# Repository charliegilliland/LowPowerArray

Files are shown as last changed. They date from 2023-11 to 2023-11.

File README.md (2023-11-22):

# LowPowerArray

This repository contains the hardware design files and firmware for a low-power acoustic array.
Up to 8 channels of microphone data are sampled at 48kHz and saved to an SD card.
Data acquisition is synchronized to UTC time with a GPS.

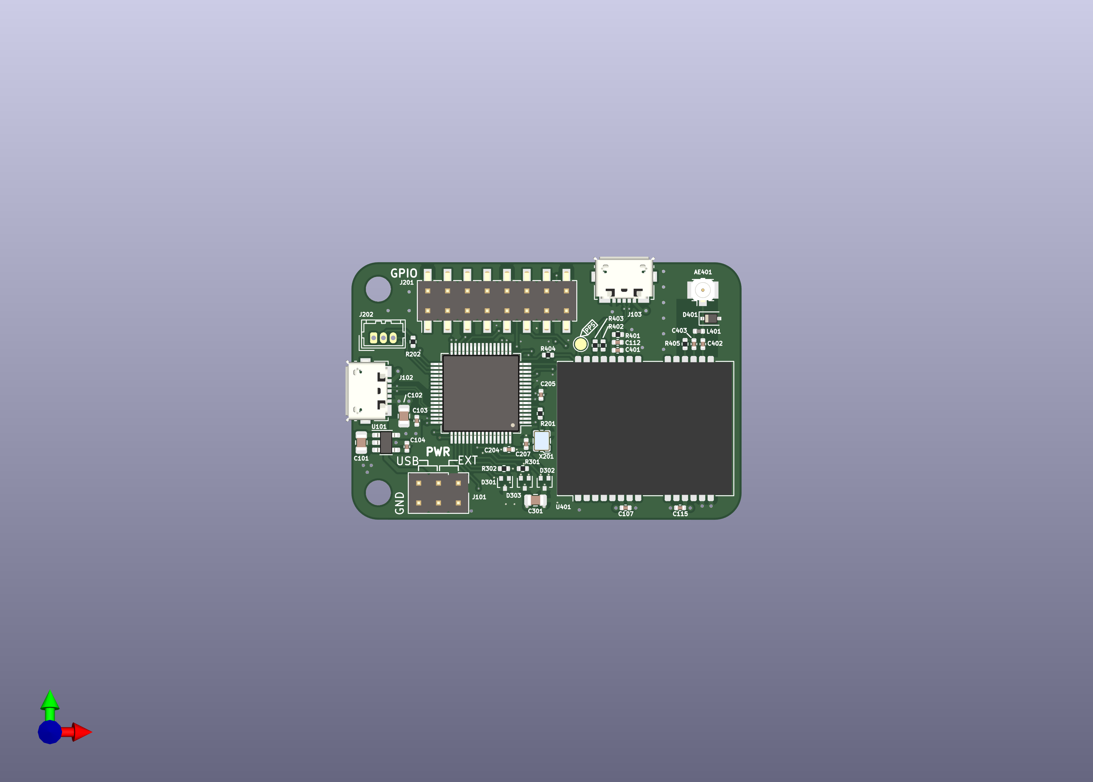
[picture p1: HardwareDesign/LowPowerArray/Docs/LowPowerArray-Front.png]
LowPowerArray


## Theory of Operation

### Power
The LowPowerArray can be powered via USB or pin headers on J101.
The power source is selected by placement of a jumper on J101.
A servo-style connector can be plugged into J101.
Refer to the schematics in [HardwareDesign](HardwareDesign/LowPowerArray/) for pin descriptions.

### Modes
There are two modes of operation: Manual and Automatic.
The mode is selected with a jumper on J201.

In Manual mode (jumper present) data acquisition is started and stopped using the pushbutton connected to J202.

In Automatic mode (jumper not present) data acquisition will begin automatically once power is applied and the GPS is locked.
If the button is pressed while in Automatic mode, the data acquisition will be stopped and the device will revert to Manual mode.

### Status
At startup, the device will wait for a GPS lock, unless ```GPS_WAIT_LOCK``` is defined as 0 (useful for lab testing).
When the GPS is locked, the LED will quickly illuminate several times, indicating that it is ready to start data acquisition.

While the data acquisition is running, the LED will illuminate every other second.

Status messages will be printed over the UART pins on J201, and also over USB via the virtual COM port.

### Programming
The STM32 microcontroller is programmed via SWD using the pins SWDIO, SWCLK, NRST on J201.
A Nucleo development board, or dedicated programmer, can be used to program the device.

### Microphone Connections
The 10-pin FFC connector, J1, is used to connect to a microphone board.

Alternatively, the BCLK, FSYNC, and DATA pins are available as pin headers on J201.

### SD Card Storage
Audio and GPS data are stored on the microSD card.
The card must be formatted as exFAT.

At startup, the device will create a new directory with the prefix ```filesXXXX```, where XXXX is a number: i.e. ```files0001```.

Audio and GPS files will be stored in the newly created directory, with file names ```audioXXXX.pcm``` and ```gpsXXXX.txt```.
Audio data is raw PCM format, with 8 channels and 32-bit word length.
GPS data is stored as plain text NMEA sentences, exactly as it is received from the GPS module.

GPS data can be tied to the audio data by matching the file numbers.
There is one pair of GPS messages for each second, where the first pair of GPS messages is tied to the first frame of audio in the audio file.

### GPS Module
The GPS module provides the PPS (pulse per second) and BCLK (bit clock) signals, as well as location and time via NMEA messages over UART.

Be sure to program the GPS module using the configuration file ```charlie-m8t-lowpower.txt```.

There is a battery connector, labeled BT101, which can provide backup power to the GPS.
The battery should be a 3v coin-cell or equivalent, and are commonly available as CMOS batteries.

Be sure to plug in the battery with the correct polarity (+ and - are marked on the v2 board).

If for some reason the GPS is not used, an auxiliary clock source can be used by populating a 12.288MHz crystal oscillator X501.
If this is used, select the clock source by placing R502 instead of R501.
Using the auxiliary clock source will require firmware changes to account for the missing PPS signal, and no GPS messages.
At time of writing this is not supported by the firmware.

For debugging purposes, when GPS lock is not required to start data acquisition, go to the file ```gps_mgr.h``` and change ```GPS_WAIT_LOCK``` to 0,
and re-program the device.
This will allow you to test the device in the lab, where GPS signals are not available.

## Programming Guide

### main.c
The file [main.c](Firmware/Core/Src/main.c) mostly contains code generated by CubeIDE. This file simply initializes the peripherals, and calls the user_app_init and user_app_loop functions.
This file should not have to be changed.

### user_app.c
The file [user_app.c](Firmware/Core/Src/user_app.c) contains the high-level runtime behavior of the device.
This includes the main endless while loop, the data acquisition loop, and button and PPS callback functions.

The endless while loop in user_app_loop implements the state diagram described below.

### aud_mgr.h
The file [aud_mgr.h](Firmware/Core/Inc/aud_mgr.h) contains the audio-specific code.
This uses the SAI peripheral in DMA mode, so that audio data can be received 'in the background' while the CPU is working on other tasks.

The ```HAL_SAI_RxCpltCallback``` is called by the hardware when a buffer of new data is ready.
In this function, the DMA buffer pointer is changed to the next buffer in the ring buffer.
The ring buffer allows for multiple buffers to be stored before they are written to the SD card. 

If there is an SAI error, or ring buffer overflow, the data acquisition will be stopped and the PPS will be re-synchronized.

### sd_mgr.h
The file [sd_mgr.h](Firmware/Core/Inc/sd_mgr.h) contains the sd card-specific code.
This code contains functions for starting new files, and writing to existing files.

### gps_mgr.h
The file [gps_mgr.h](Firmware/Core/Inc/gps_mgr.h) contains the GPS-specific code.
GPS data is received over USART2 in DMA mode.

When the GPS messages have been received, the ```HAL_UARTEx_RxEventCallback``` function will be called by the hardware.
The received messages will be copied to local buffers, and the RX will be restarted to handle the next message.

### inline functions
Many of the functions implemented in the peripheral files are ```inline``` functions.
This is done for execution speed: basically instead of actually calling those functions,
the compiler will copy that code to where the function was called.

### DAQ State Diagram
This figure describes the various states that the device can be in, and the events that cause a state change.
The ```daq_stat``` variable declared in user_app.c is used to read and change state in the code.

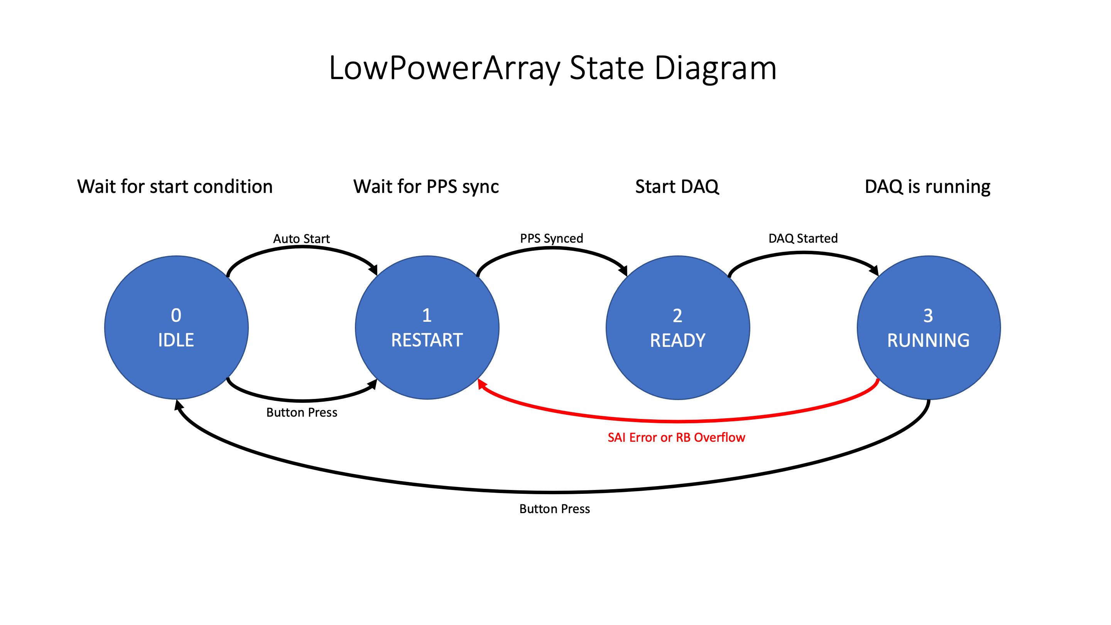
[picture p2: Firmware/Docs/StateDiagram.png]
State Diagram


## Future Work

### Directory / file naming
It would probably be better to name the files using the UTC date and time as received from the GPS.
This would require parsing each GPS message, and some more logic for dealing with the timing in creating the files.

### Control and monitoring over UART / USB
It might be possible to start and stop the data acquisition over UART or USB, though I haven't explored this in detail.
This would allow a remote computer, such as a raspberry pi, to control the data acquisition.
Additionally, a telemetry radio could be connected to the UART serial port for remote status monitoring and control.

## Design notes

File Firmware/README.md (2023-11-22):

# LowPowerArrayFirmware

This repository contains the STM32CubeIDE project files used on the LowPowerArray board.

## Theory of Operation

### Power
The LowPowerArray can be powered via USB or pin headers on J101.
The power source is selected by placement of a jumper on J101.
A servo-style connector can be plugged into J101.
Refer to the schematics in [Charlie-KiCad](https://github.com/UM-NCPA/Charlie-KiCad/tree/main/LowPowerArray_v2) for pin descriptions.

### Modes
There are two modes of operation: Manual and Automatic.
The mode is selected with a jumper on J201.

In Manual mode (jumper present) data acquisition is started and stopped using the pushbutton connected to J202.

In Automatic mode (jumper not present) data acquisition will begin automatically once power is applied and the GPS is locked.
If the button is pressed while in Automatic mode, the data acquisition will be stopped and the device will revert to Manual mode.

### Status
At startup, the device will wait for a GPS lock, unless ```GPS_WAIT_LOCK``` is defined as 0 (useful for lab testing).
When the GPS is locked, the LED will quickly illuminate several times, indicating that it is ready to start data acquisition.

While the data acquisition is running, the LED will illuminate every other second.

Status messages will be printed over the UART pins on J201, and also over USB via the virtual COM port.

### Programming
The STM32 microcontroller is programmed via SWD using the pins SWDIO, SWCLK, NRST on J201.
A Nucleo development board, or dedicated programmer, can be used to program the device.

### Microphone Connections
The 10-pin FFC connector, J1, is used to connect to a microphone board.

Alternatively, the BCLK, FSYNC, and DATA pins are available as pin headers on J201.

### SD Card Storage
Audio and GPS data are stored on the microSD card.
The card must be formatted as exFAT.

At startup, the device will create a new directory with the prefix ```filesXXXX```, where XXXX is a number: i.e. ```files0001```.

Audio and GPS files will be stored in the newly created directory, with file names ```audioXXXX.pcm``` and ```gpsXXXX.txt```.
Audio data is raw PCM format, with 8 channels and 32-bit word length.
GPS data is stored as plain text NMEA sentences, exactly as it is received from the GPS module.

GPS data can be tied to the audio data by matching the file numbers.
There is one pair of GPS messages for each second, where the first pair of GPS messages is tied to the first frame of audio in the audio file.

### GPS Module
The GPS module provides the PPS (pulse per second) and BCLK (bit clock) signals, as well as location and time via NMEA messages over UART.

Be sure to program the GPS module using the configuration file ```charlie-m8t-lowpower.txt```.

There is a battery connector, labeled BT101, which can provide backup power to the GPS.
The battery should be a 3v coin-cell or equivalent, and are commonly available as CMOS batteries.

Be sure to plug in the battery with the correct polarity (+ and - are marked on the v2 board).

If for some reason the GPS is not used, an auxiliary clock source can be used by populating a 12.288MHz crystal oscillator X501.
If this is used, select the clock source by placing R502 instead of R501.
Using the auxiliary clock source will require firmware changes to account for the missing PPS signal, and no GPS messages.
At time of writing this is not supported by the firmware.

For debugging purposes, when GPS lock is not required to start data acquisition, go to the file ```gps_mgr.h``` and change ```GPS_WAIT_LOCK``` to 0,
and re-program the device.
This will allow you to test the device in the lab, where GPS signals are not available.

## Programming Guide

### main.c
The file [main.c](https://github.com/UM-NCPA/LowPowerArrayFirmware/blob/main/Core/Src/main.c) mostly contains code generated by CubeIDE. This file simply initializes the peripherals, and calls the user_app_init and user_app_loop functions.
This file should not have to be changed.

### user_app.c
The file [user_app.c](https://github.com/UM-NCPA/LowPowerArrayFirmware/blob/main/Core/Src/user_app.c) contains the high-level runtime behavior of the device.
This includes the main endless while loop, the data acquisition loop, and button and PPS callback functions.

The endless while loop in user_app_loop implements the state diagram described below.

### aud_mgr.h
The file [aud_mgr.h](https://github.com/UM-NCPA/LowPowerArrayFirmware/blob/main/Core/Inc/aud_mgr.h) contains the audio-specific code.
This uses the SAI peripheral in DMA mode, so that audio data can be received 'in the background' while the CPU is working on other tasks.

The ```HAL_SAI_RxCpltCallback``` is called by the hardware when a buffer of new data is ready.
In this function, the DMA buffer pointer is changed to the next buffer in the ring buffer.
The ring buffer allows for multiple buffers to be stored before they are written to the SD card. 

If there is an SAI error, or ring buffer overflow, the data acquisition will be stopped and the PPS will be re-synchronized.

### sd_mgr.h
The file [sd_mgr.h](https://github.com/UM-NCPA/LowPowerArrayFirmware/blob/main/Core/Inc/sd_mgr.h) contains the sd card-specific code.
This code contains functions for starting new files, and writing to existing files.

### gps_mgr.h
The file [gps_mgr.h](https://github.com/UM-NCPA/LowPowerArrayFirmware/blob/main/Core/Inc/gps_mgr.h) contains the GPS-specific code.
GPS data is received over USART2 in DMA mode.

When the GPS messages have been received, the ```HAL_UARTEx_RxEventCallback``` function will be called by the hardware.
The received messages will be copied to local buffers, and the RX will be restarted to handle the next message.

### inline functions
Many of the functions implemented in the peripheral files are ```inline``` functions.
This is done for execution speed: basically instead of actually calling those functions,
the compiler will copy that code to where the function was called.

### DAQ State Diagram
This figure describes the various states that the device can be in, and the events that cause a state change.
The ```daq_stat``` variable declared in user_app.c is used to read and change state in the code.

State Diagram

## Future Work

### Magnetometer / Compass
The magnetometer added in v2 of the LowPowerArray board is not yet implemented by the firmware.
It is connected to i2c1 on pins PB8 and PB9. Ideally, the magnetometer data should be read in Interrupt mode (non-blocking).
Once the magnetometer data has been received and processed, the compass heading can be written to the GPS file, preferably in plain text.
Write the compass heading to the file once per second, same as the GPS data.
An easy way to do this would be to write it right after the GPS data is written.

### Directory / file naming
It would probably be better to name the files using the UTC date and time as received from the GPS.
This would require parsing each GPS message, and some more logic for dealing with the timing in creating the files.

### Control and monitoring over UART / USB
It might be possible to start and stop the data acquisition over UART or USB, though I haven't explored this in detail.
This would allow a remote computer, such as a raspberry pi, to control the data acquisition.
Additionally, a telemetry radio could be connected to the UART serial port for remote status monitoring and control.

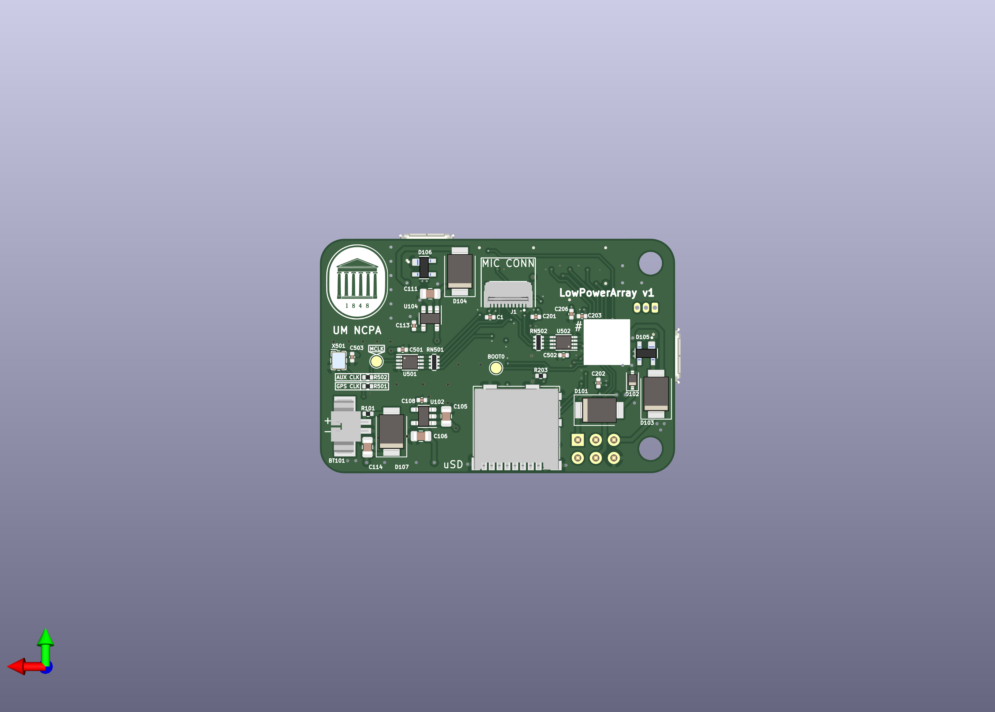
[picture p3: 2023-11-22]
HardwareDesign/LowPowerArray/Docs/LowPowerArray-Back.png

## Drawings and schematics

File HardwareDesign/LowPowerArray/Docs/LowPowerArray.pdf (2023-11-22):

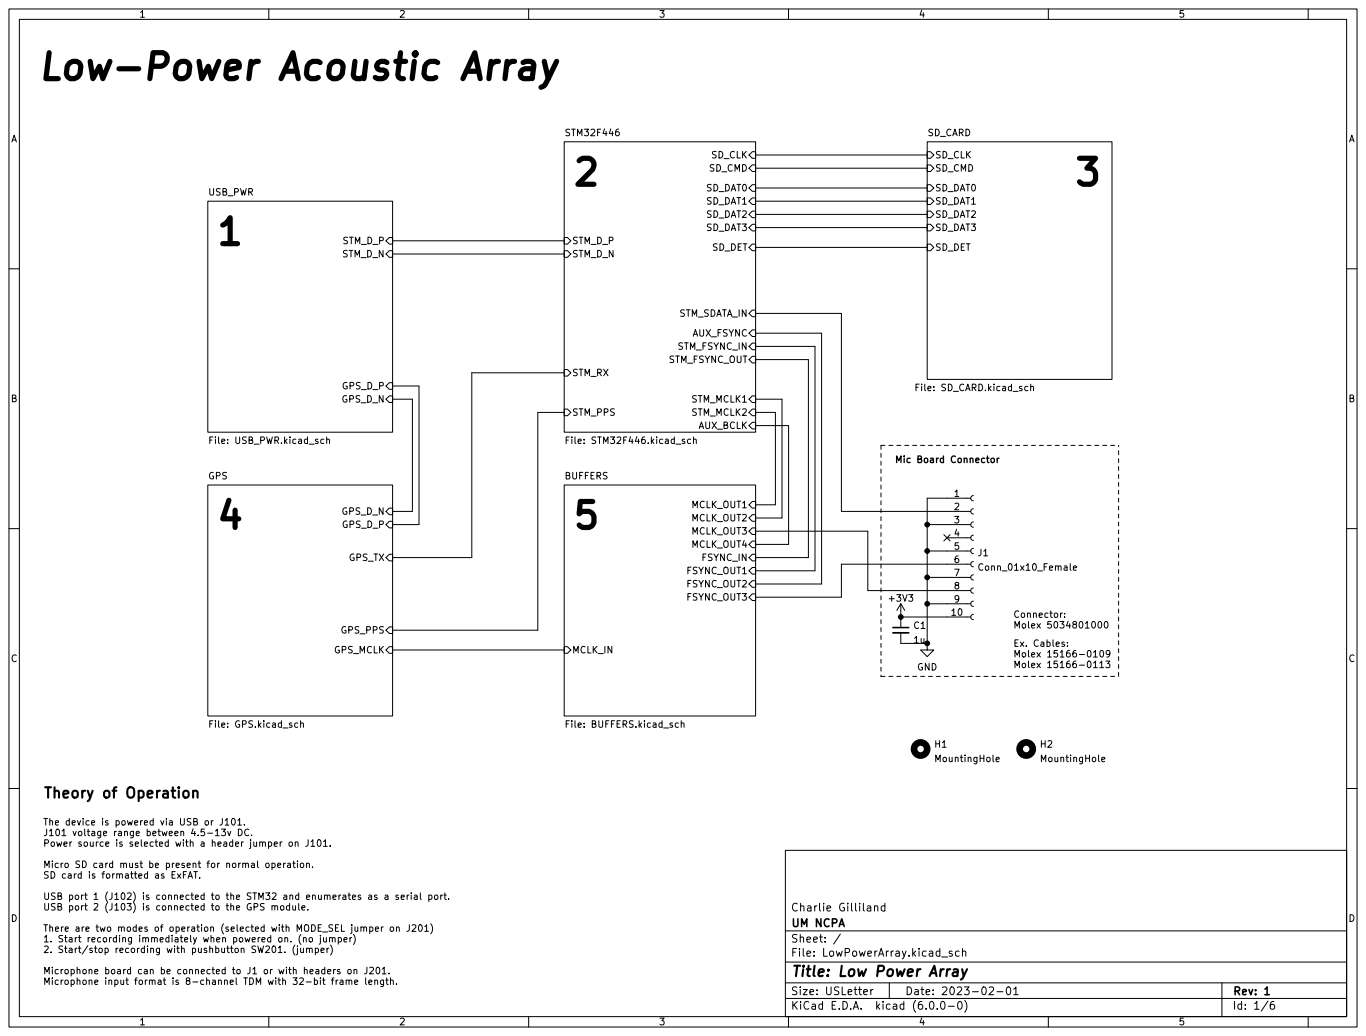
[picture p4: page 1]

Low-Power Acoustic Array

Ex. Cables: Molex 15166-0109 Molex 15166-0113 Connector: Molex 5034801000 5

The device is powered via USB or J101.
J101 voltage range between 4.5-13v DC.
Power source is selected with a header jumper on J101.

Micro SD card must be present for normal operation. SD card is formatted as ExFAT. USB port 1 (J102) is connected to the STM32 and enumerates as a serial port.

USB port 2 (J103) is connected to the GPS module.
There are two modes of operation (selected with MODE_SEL jumper on J201)
1. Start recording immediately when powered on. (no jumper)
2. Start/stop recording with pushbutton SW201. (jumper)

Charlie Gilliland
File: LowPowerArray.kicad_sch Sheet: / UM NCPA

Microphone board can be connected to J1 or with headers on J201.
Microphone input format is 8-channel TDM with 32-bit frame length.

Id: 1/6 Title: Low Power Array

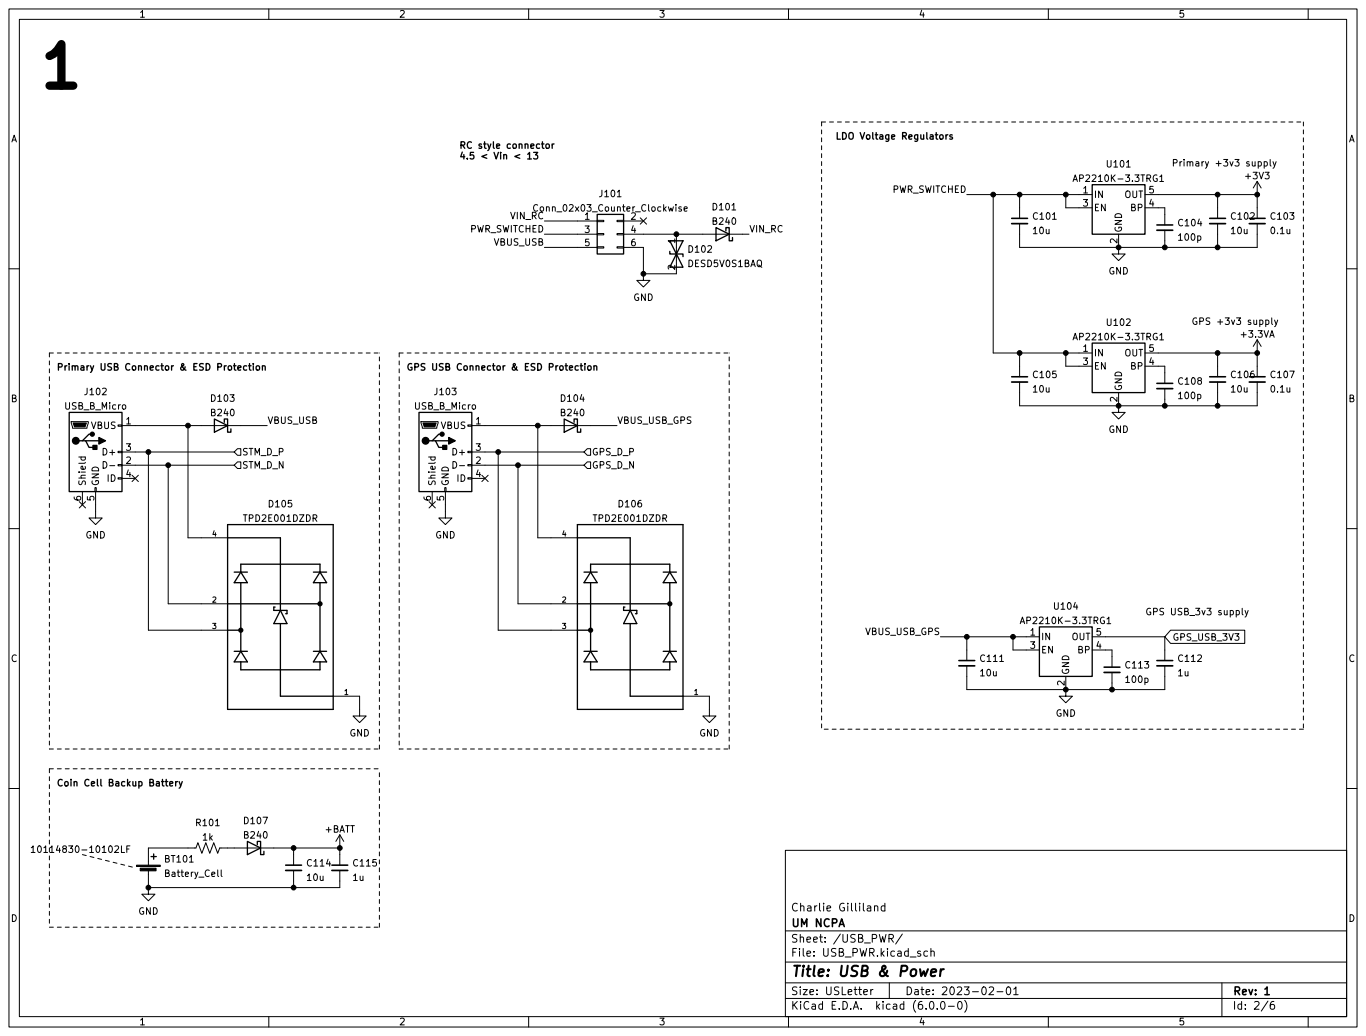
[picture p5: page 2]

2 EN 3 BP 4 OUT 5 U101 AP2210K-3.3TRG1 +3V3 GND

2 EN 3 BP 4 OUT 5 U102 AP2210K-3.3TRG1 GND

10114830-10102LF Coin Cell Backup Battery

File: USB_PWR.kicad_sch
Id: 2/6 Title: USB & Power

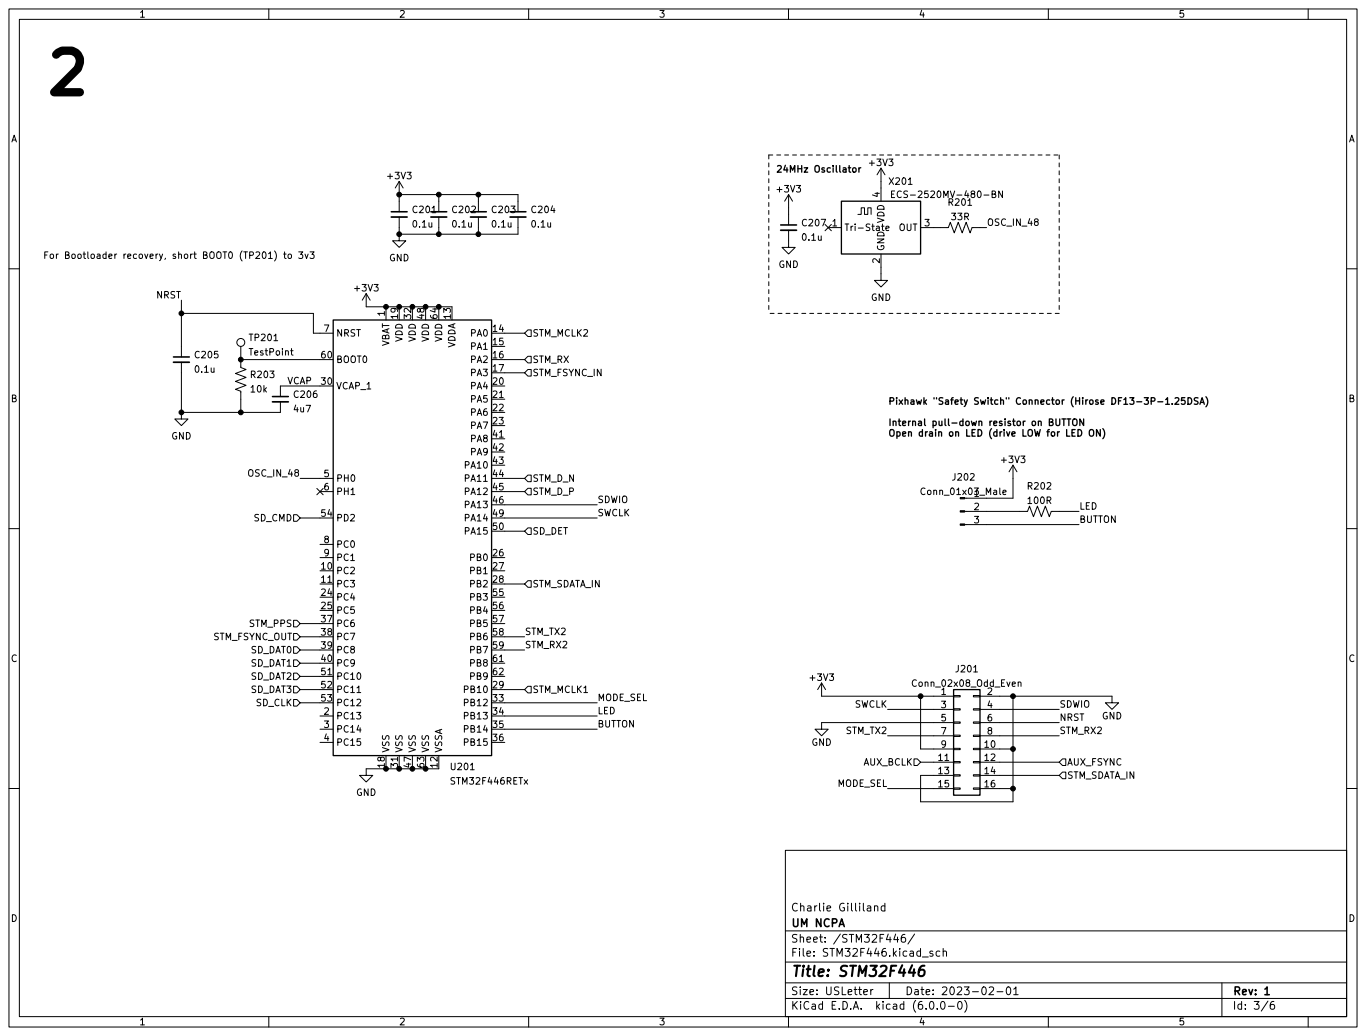
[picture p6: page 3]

For Bootloader recovery, short BOOT0 (TP201) to 3v3

1 PC2 10 PC3 11 VSSA 12 VDDA 13 PA0 14 PA1 15 PA2 16 PA3 17 VSS 18 VDD 19 PC13 2 PA4 20 PA5 21 PA6 22 PA7 23 PC4 24 PC5 25 PB0 26 PB1 27 PB2 28 PB10 29 PC14 3 VCAP_1 30 VSS 31 VDD 32 PB12 33 PB13 34 PB14 35 PB15 36 PC6 37 PC7 38 PC8 39 PC15 4 PC9 40 PA8 41 PA9 42 PA10 43 PA11 44 PA12 45 PA13 46 VSS 47 VDD 48 PA14 49 PH0 5 PA15 50 PC10 51 PC11 52 PC12 53 PD2 54 PB3 55 PB4 56 PB5 57 PB6 58 PB7 59 PH1 6 BOOT0 60 PB8 61 PB9 62 VSS 63 VDD 64 NRST 7 PC0 8 PC1 9 U201 STM32F446RETx 1

Internal pull-down resistor on BUTTON
Open drain on LED (drive LOW for LED ON)

9 | 10

Charlie Gilliland
File: STM32F446.kicad_sch Sheet: /STM32F446/ UM NCPA

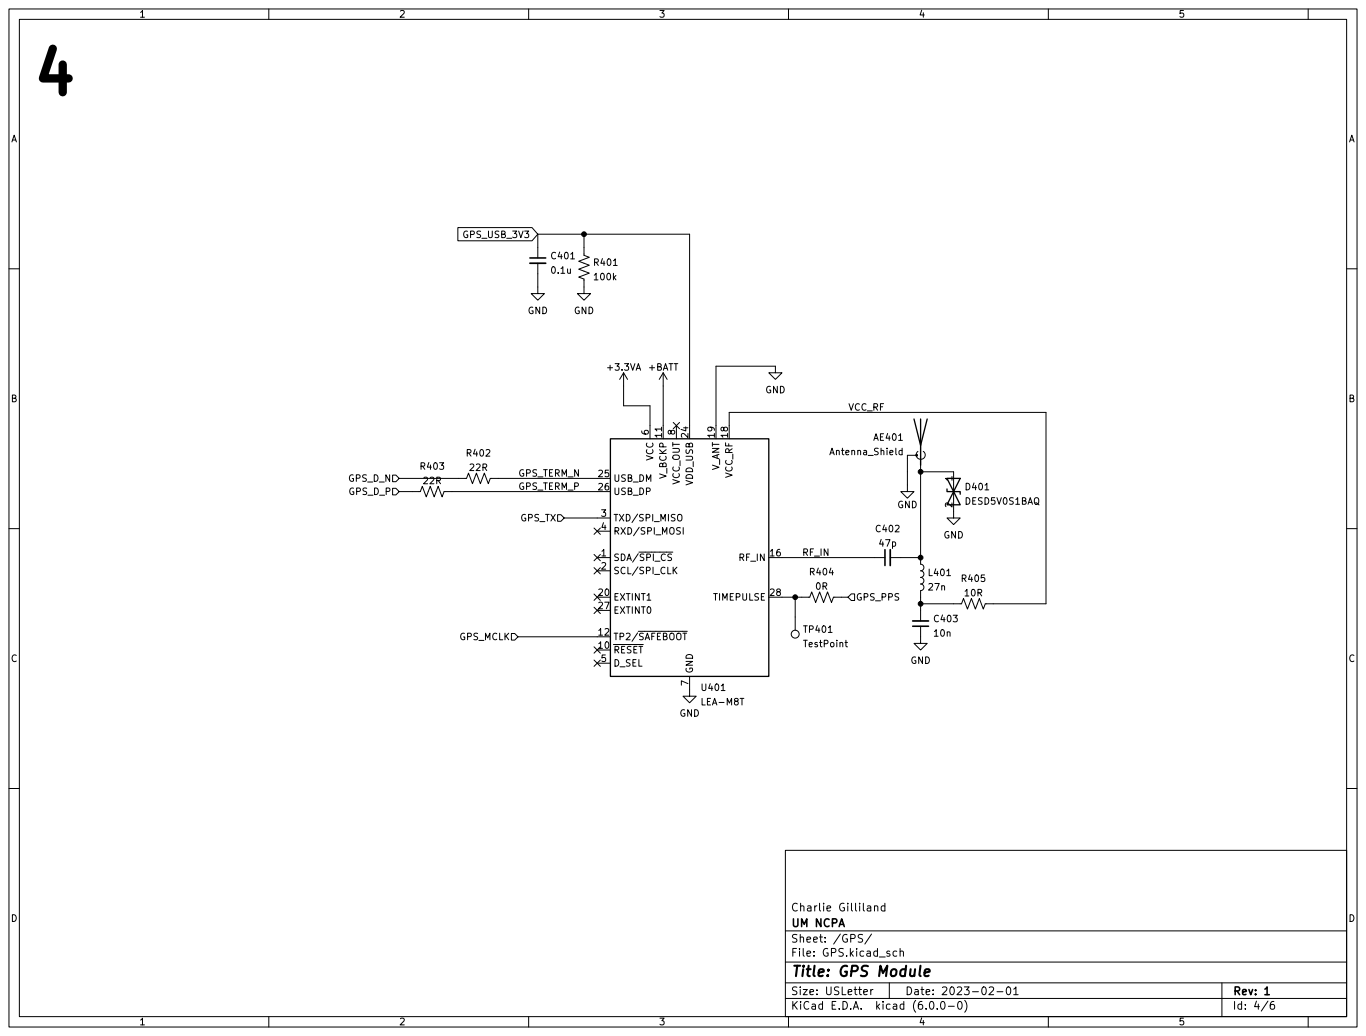
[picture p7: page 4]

File: GPS.kicad_sch Sheet: /GPS/ UM NCPA

Id: 4/6 Title: GPS Module

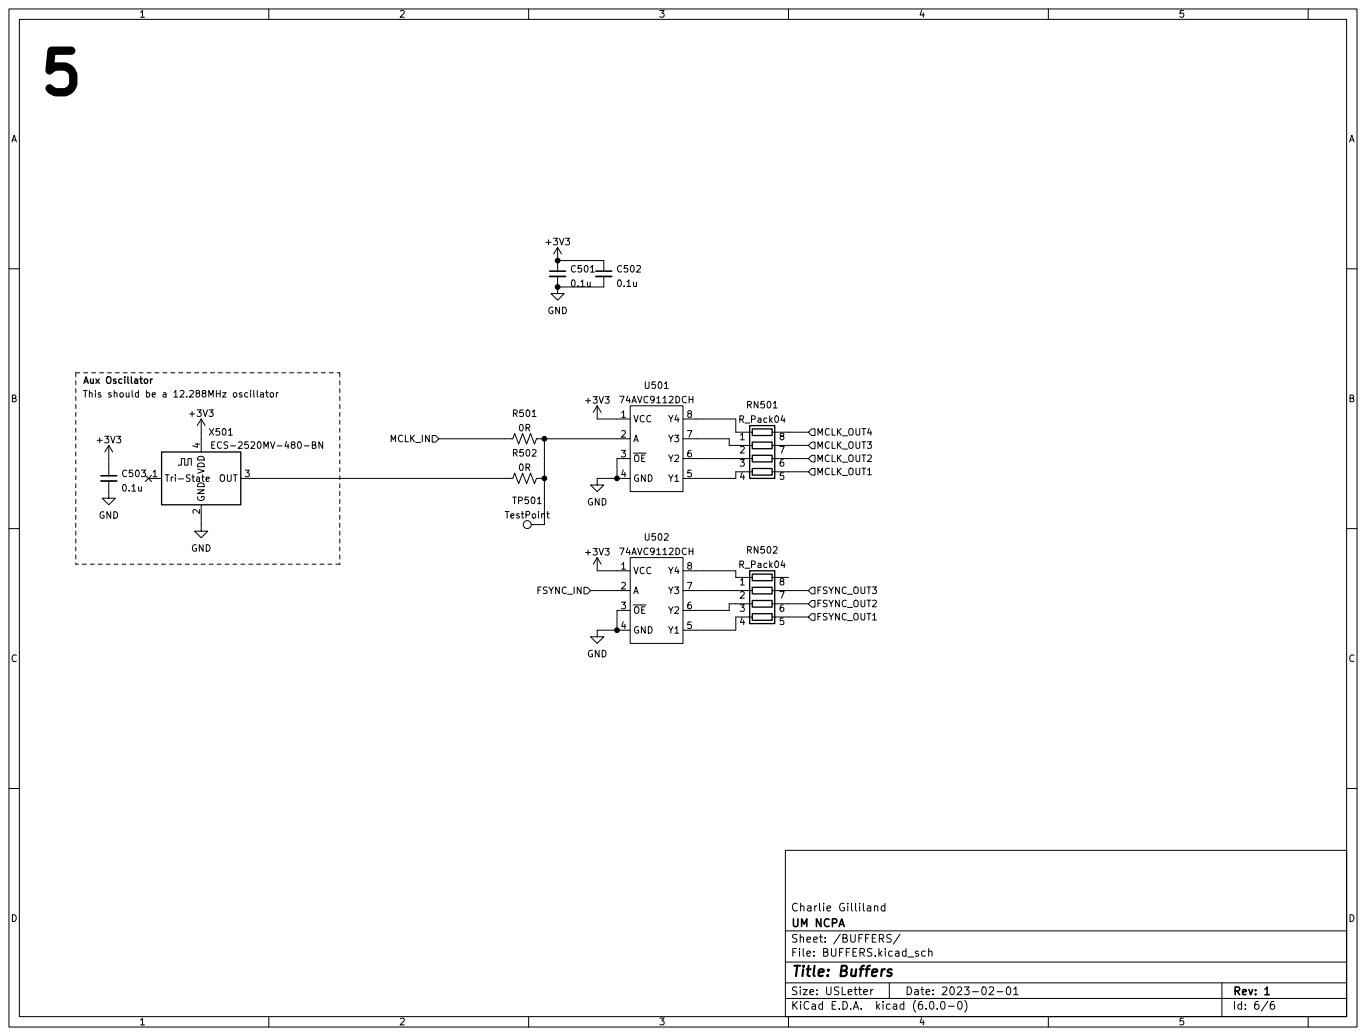
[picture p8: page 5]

Aux Oscillator This should be a 12.288MHz oscillator
0.1u +3V3 GND

Charlie Gilliland
File: BUFFERS.kicad_sch Sheet: /BUFFERS/ UM NCPA

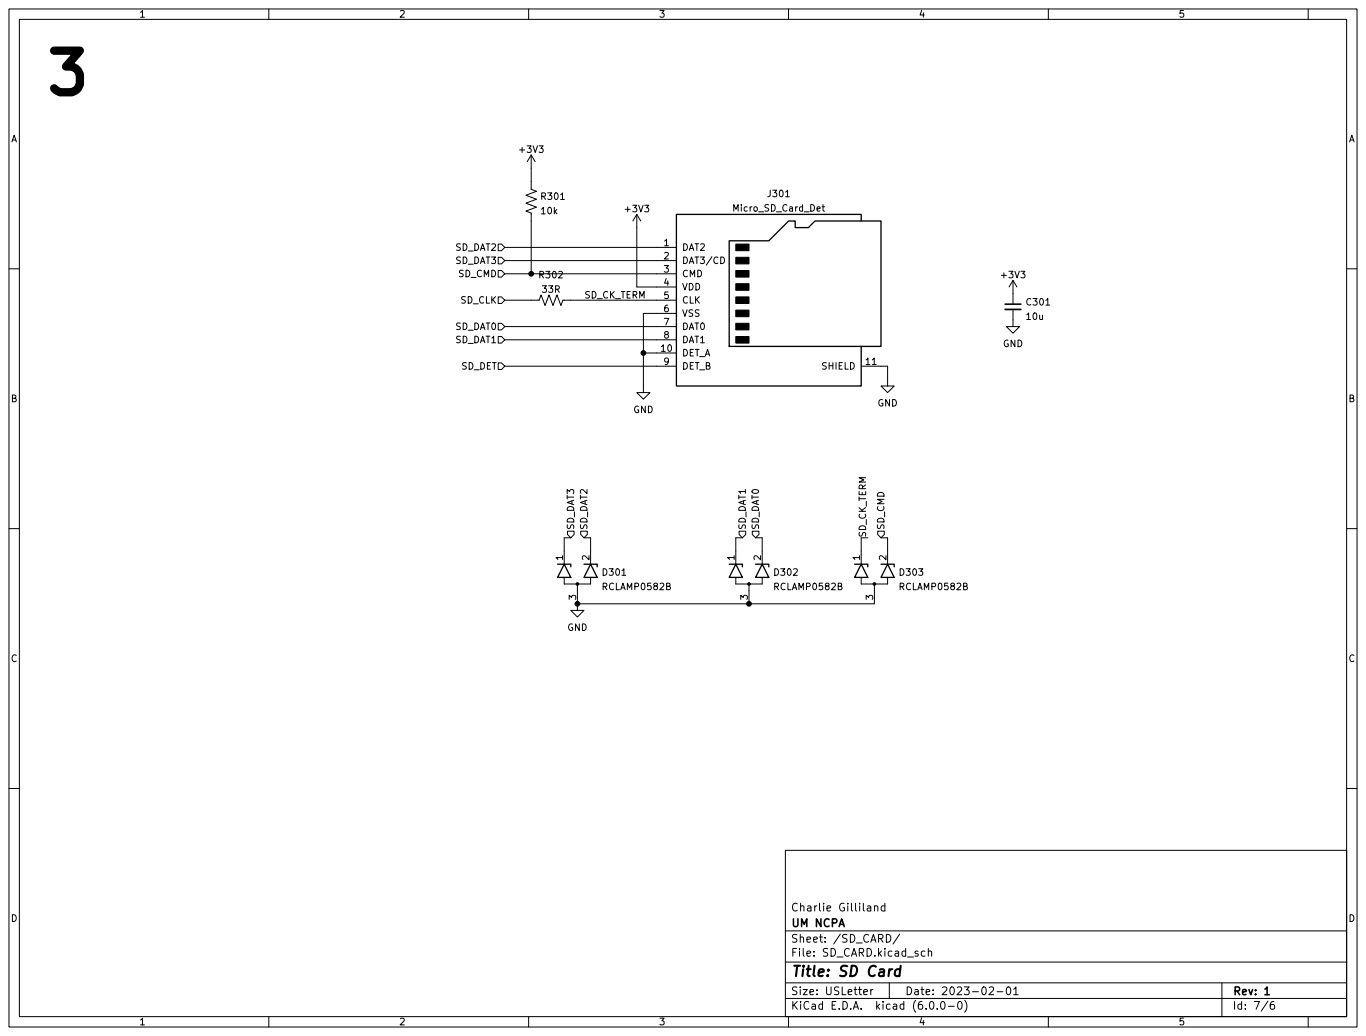
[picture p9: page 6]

File: SD_CARD.kicad_sch
Id: 7/6 Title: SD Card

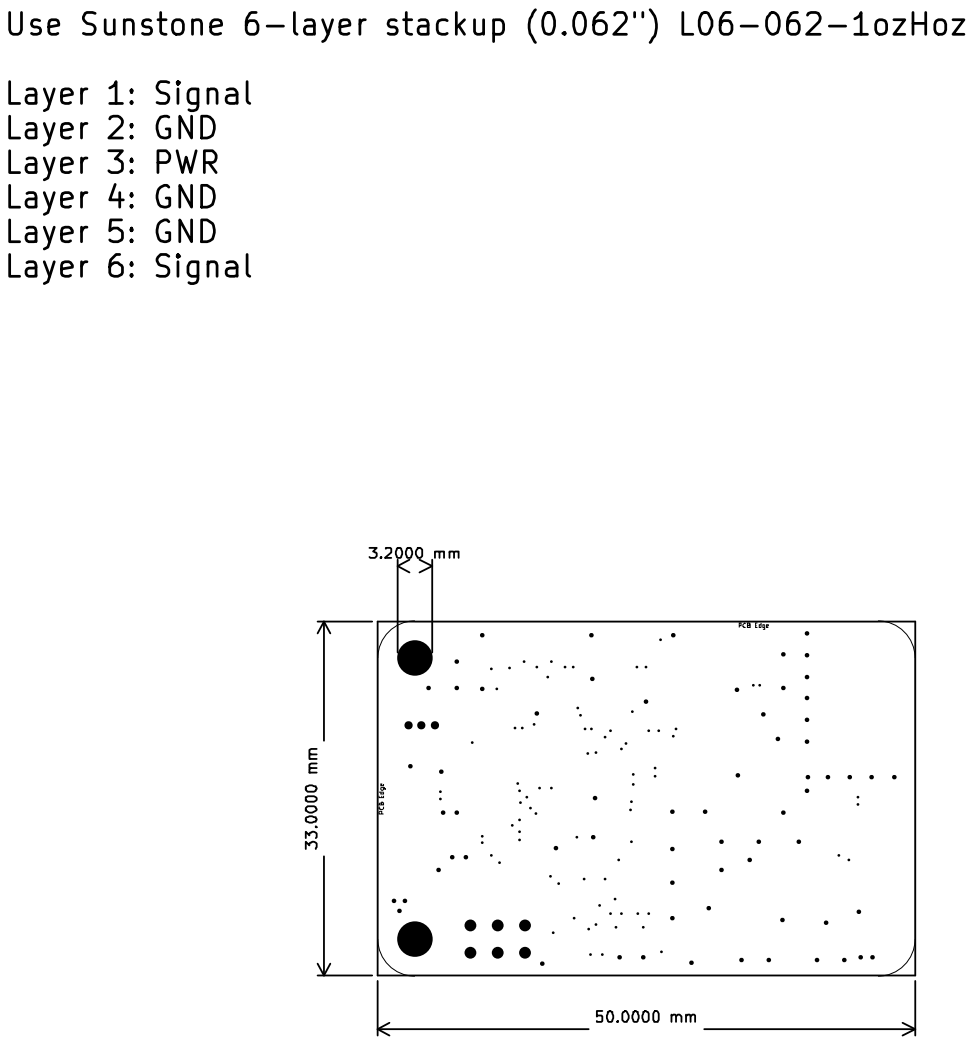
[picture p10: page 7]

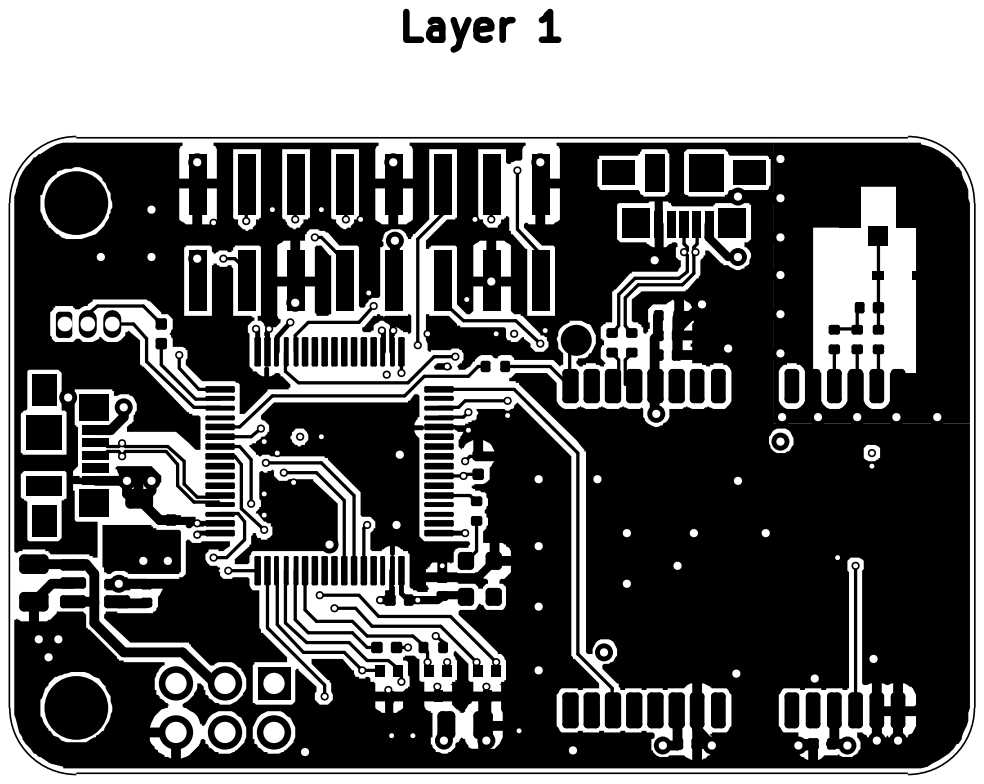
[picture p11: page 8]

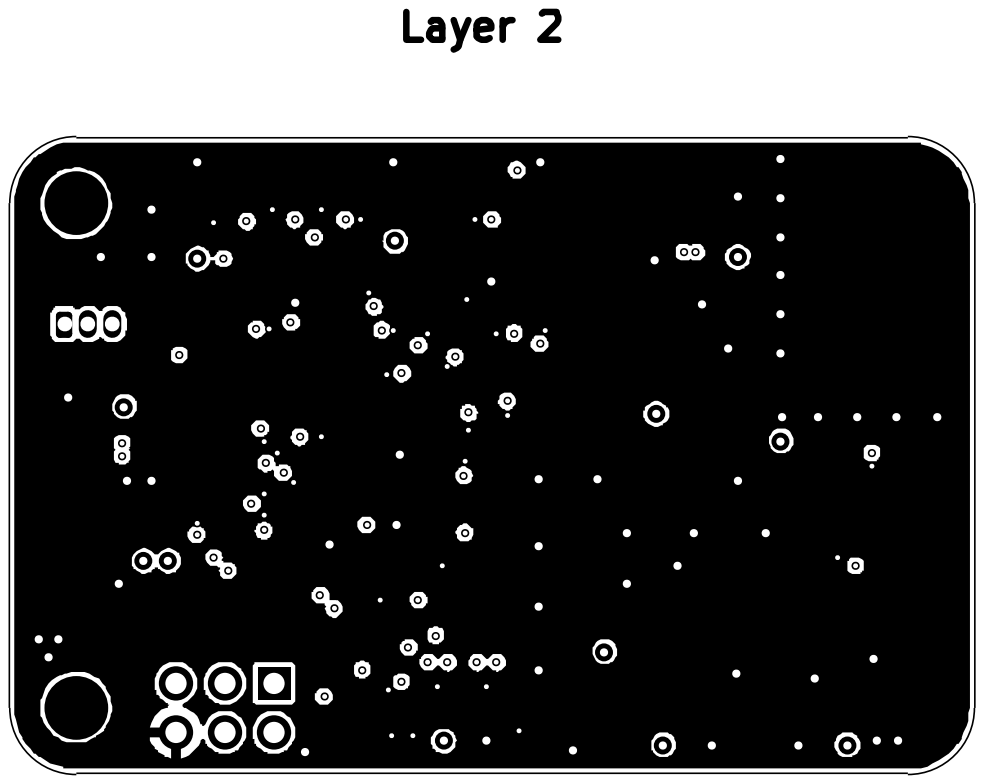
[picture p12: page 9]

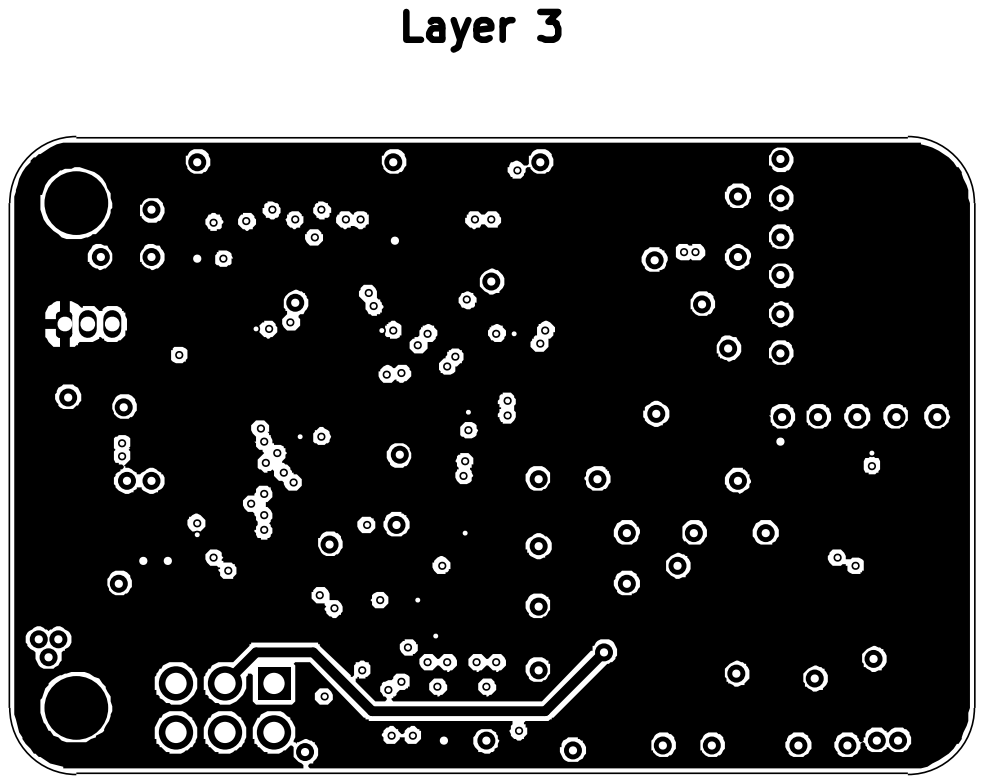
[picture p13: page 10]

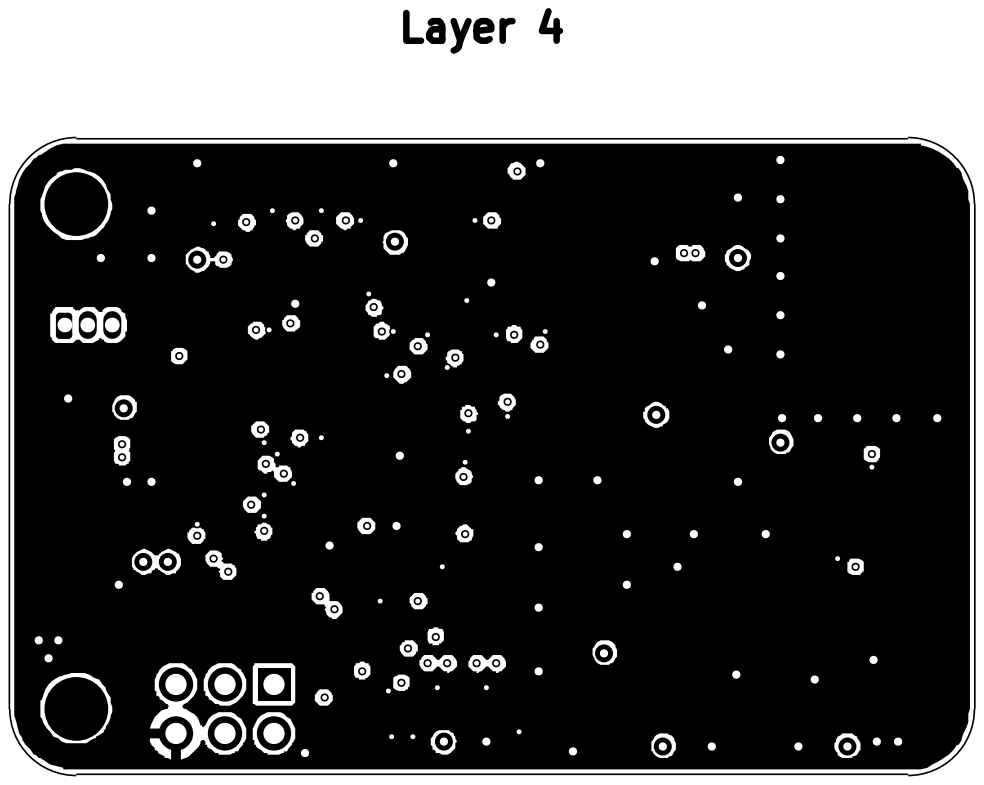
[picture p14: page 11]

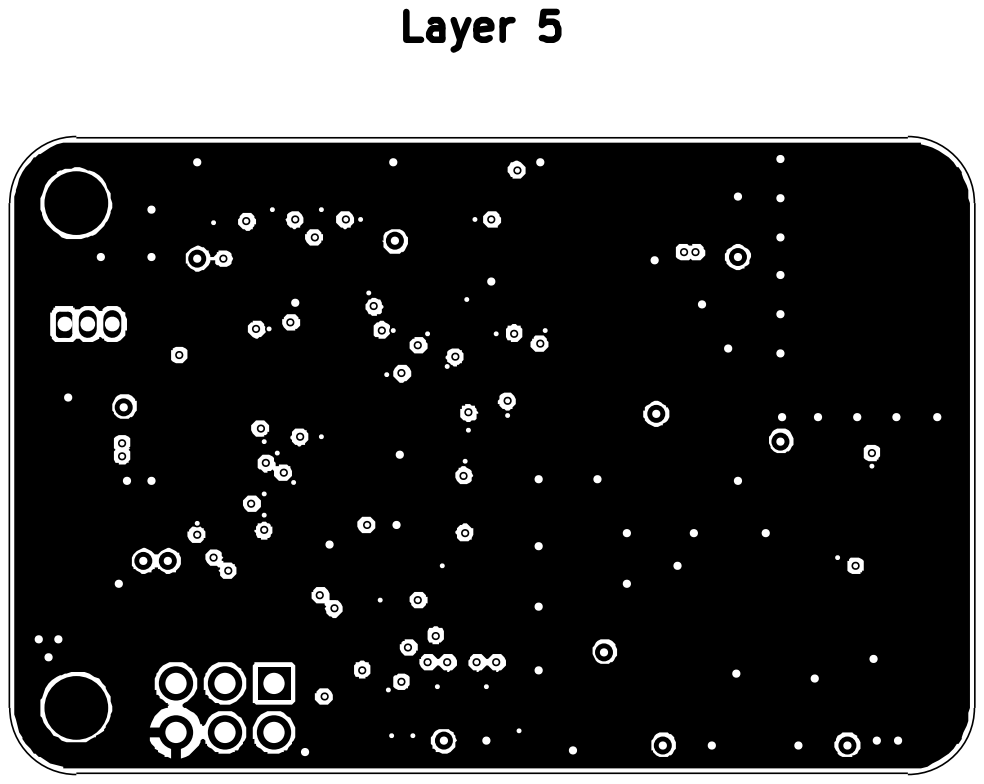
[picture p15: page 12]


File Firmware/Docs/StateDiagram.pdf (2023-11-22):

# LowPowerArray State Diagram

0 IDLE; 1 RESTART; 2 READY; 3 RUNNING; Wait for start condition; Wait for PPS sync; Start DAQ; DAQ is running; Auto Start; PPS Synced; DAQ Started; Button Press

SAI Error or RB Overflow

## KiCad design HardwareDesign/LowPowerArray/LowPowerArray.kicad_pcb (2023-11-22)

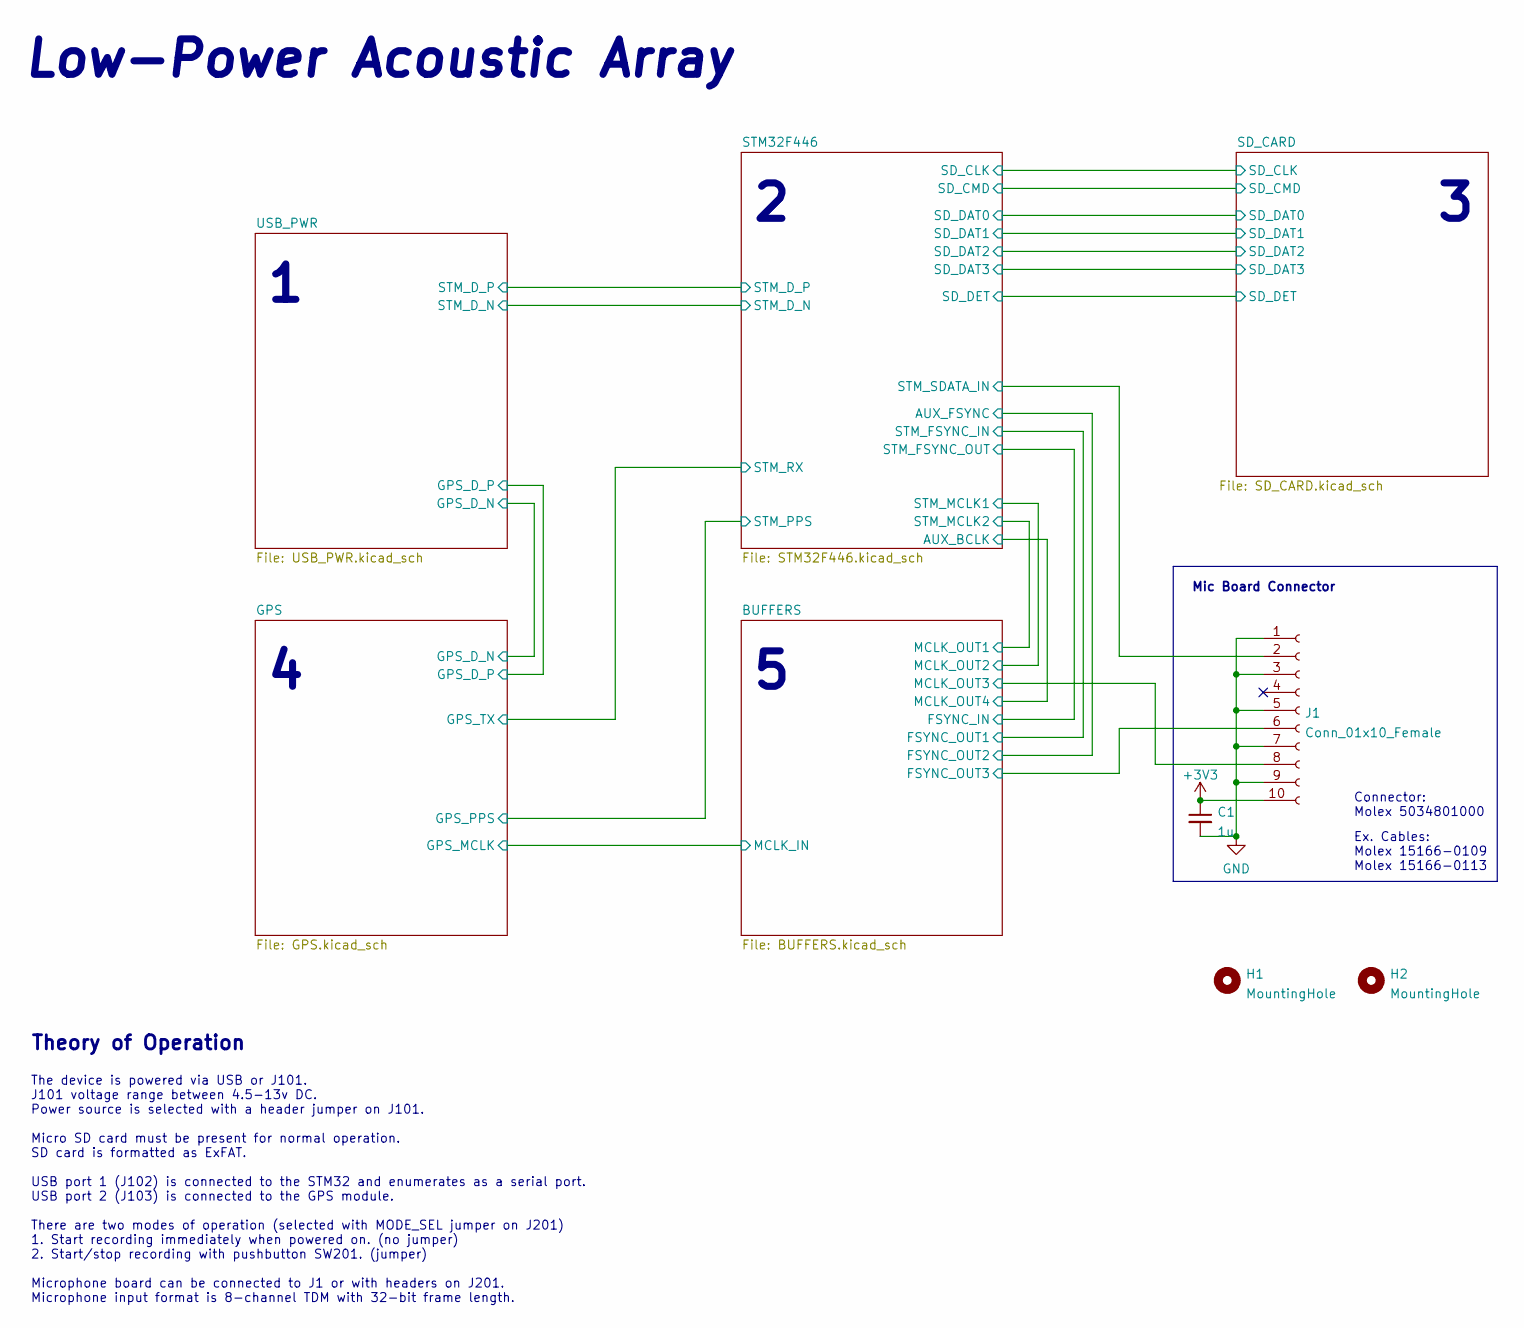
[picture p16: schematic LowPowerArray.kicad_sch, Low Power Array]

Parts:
C1: 1u; C_0402_1005Metric
H1, H2: MountingHole; MountingHole_3.2mm_M3
J1: Conn_01x10_Female; MOLEX_5034801000

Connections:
+3V3: C1.1, J1.10; also elsewhere on the board
/BUFFERS/FSYNC_OUT3: J1.6; also elsewhere on the board
/BUFFERS/MCLK_OUT3: J1.8; also elsewhere on the board
/STM32F446/STM_SDATA_IN: J1.2; also elsewhere on the board
GND: C1.2, J1.1, J1.3, J1.5, J1.7, J1.9; also elsewhere on the board

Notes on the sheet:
The device is powered via USB or J101. J101 voltage range between 4.5-13v DC. Power source is selected with a header jumper on J101. Micro SD card must be present for normal operation. SD card is formatted as ExFAT. USB port 1 (J102) is connected to the STM32 and enumerates as a serial port. USB po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
Connector: Molex 5034801000
Theory of Operation
Mic Board Connector
Low-Power Acoustic Array
Ex. Cables: Molex 15166-0109 Molex 15166-0113

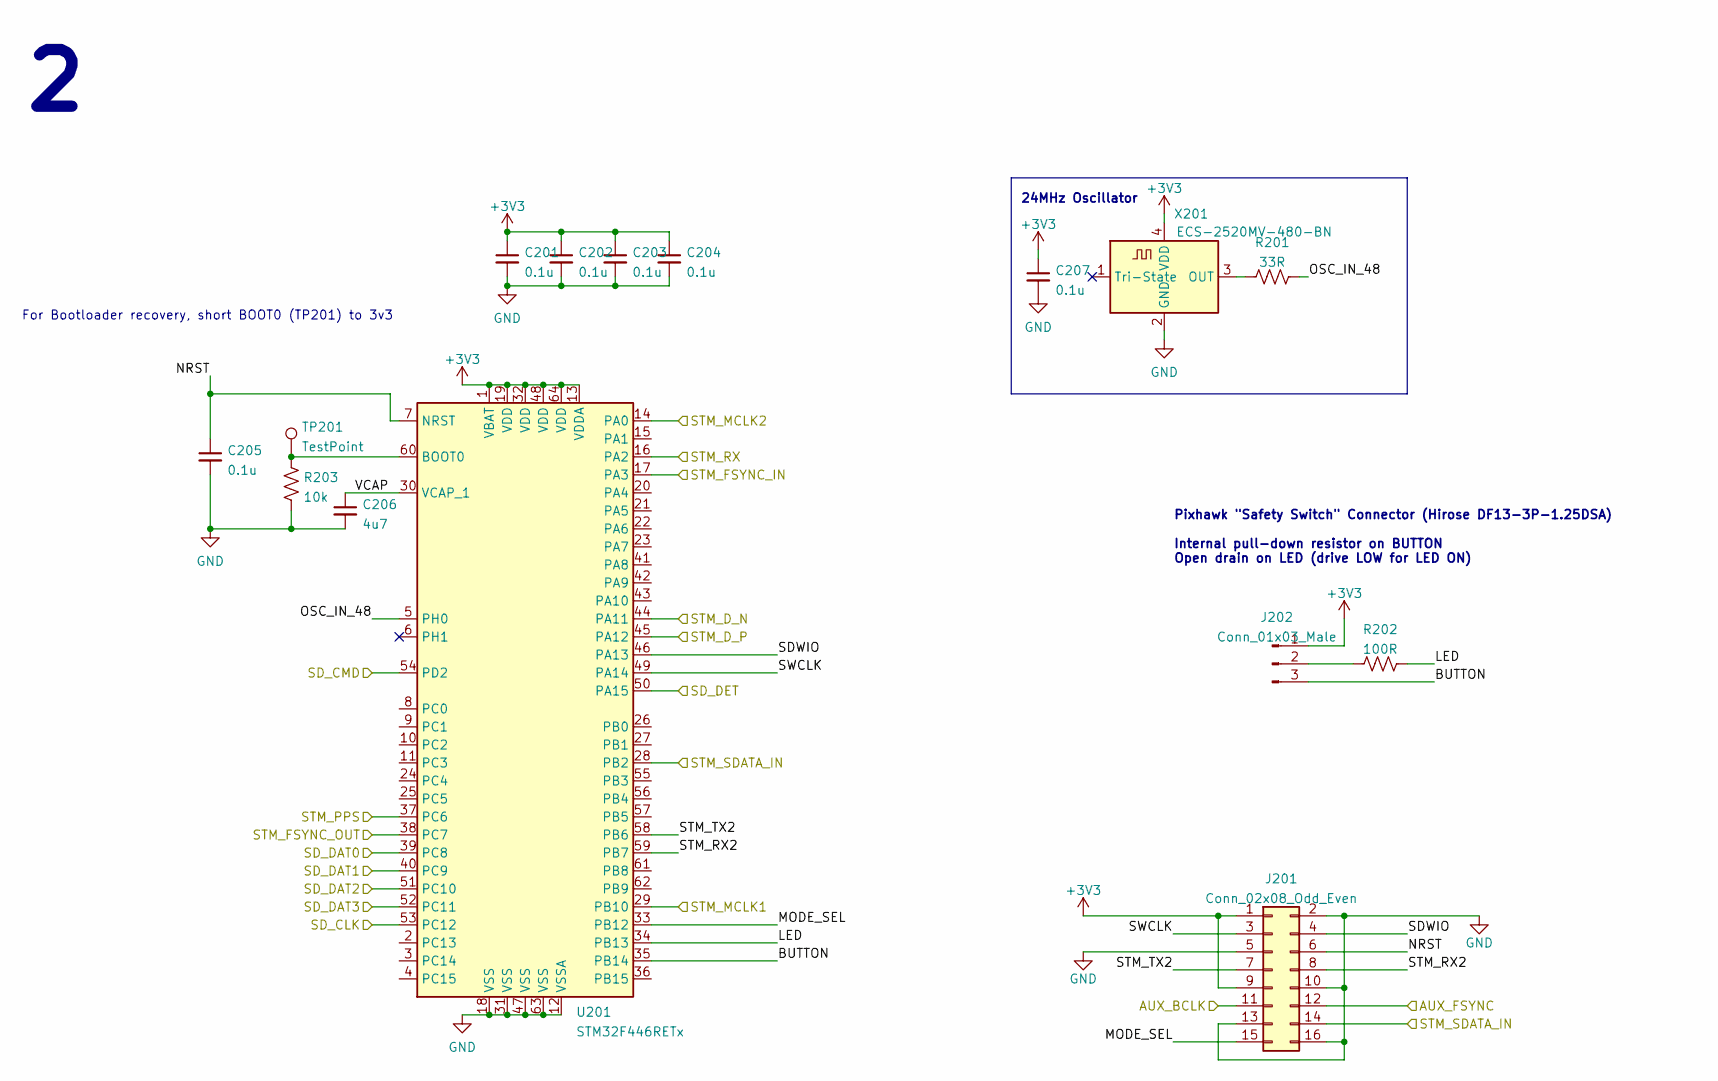
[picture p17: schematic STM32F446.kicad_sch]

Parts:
C201, C202, C203, C204, C205, C207: 0.1u; C_0402_1005Metric
C206: 4u7; C_0402_1005Metric
J201: Conn_02x08_Odd_Even; PinHeader_2x08_P2.54mm_Vertical_SMD
J202: Conn_01x03_Male; Hirose_DF13-03P-1.25DSA_1x03_P1.25mm_Vertical
R201: 33R; R_0402_1005Metric
R202: 100R; R_0402_1005Metric
R203: 10k; R_0402_1005Metric
TP201: TestPoint; TestPoint_Pad_D1.5mm
U201: STM32F446RETx; LQFP-64_10x10mm_P0.5mm
X201: ECS-2520MV-480-BN; Oscillator_SMD_ECS_2520MV-xxx-xx-4Pin_2.5x2.0mm

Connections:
+3V3: C201.1, C202.1, C203.1, C204.1, C207.1, J201.1, J201.9, J202.1, U201.1 (VBAT), U201.13 (VDDA), U201.19 (VDD), U201.32 (VDD), U201.48 (VDD), U201.64 (VDD), X201.4 (VDD); also elsewhere on the board
/BUFFERS/FSYNC_IN: U201.38 (PC7); also elsewhere on the board
/BUFFERS/FSYNC_OUT1: U201.17 (PA3); also elsewhere on the board
/BUFFERS/FSYNC_OUT2: J201.12; also elsewhere on the board
/BUFFERS/MCLK_OUT1: U201.14 (PA0); also elsewhere on the board
/BUFFERS/MCLK_OUT2: U201.29 (PB10); also elsewhere on the board
/BUFFERS/MCLK_OUT4: J201.11; also elsewhere on the board
/GPS/GPS_PPS: U201.37 (PC6); also elsewhere on the board
/GPS/GPS_TX: U201.16 (PA2); also elsewhere on the board
/SD_CARD/SD_CLK: U201.53 (PC12); also elsewhere on the board
/SD_CARD/SD_CMD: U201.54 (PD2); also elsewhere on the board
/SD_CARD/SD_DAT0: U201.39 (PC8); also elsewhere on the board
/SD_CARD/SD_DAT1: U201.40 (PC9); also elsewhere on the board
/SD_CARD/SD_DAT2: U201.51 (PC10); also elsewhere on the board
/SD_CARD/SD_DAT3: U201.52 (PC11); also elsewhere on the board
/SD_CARD/SD_DET: U201.50 (PA15); also elsewhere on the board
/STM32F446/BUTTON: J202.3, U201.35 (PB14)
/STM32F446/LED: R202.2, U201.34 (PB13)
/STM32F446/MODE_SEL: J201.15, U201.33 (PB12)
/STM32F446/NRST: C205.1, J201.6, U201.7 (NRST)
/STM32F446/OSC_IN_48: R201.2, U201.5 (PH0)
/STM32F446/SDWIO: J201.4, U201.46 (PA13)
/STM32F446/STM_D_N: U201.44 (PA11); also elsewhere on the board
/STM32F446/STM_D_P: U201.45 (PA12); also elsewhere on the board
/STM32F446/STM_RX2: J201.8, U201.59 (PB7)
/STM32F446/STM_SDATA_IN: J201.14, U201.28 (PB2); also elsewhere on the board
/STM32F446/STM_TX2: J201.7, U201.58 (PB6)
/STM32F446/SWCLK: J201.3, U201.49 (PA14)
/STM32F446/VCAP: C206.1, U201.30 (VCAP_1)
GND: C201.2, C202.2, C203.2, C204.2, C205.2, C206.2, C207.2, J201.2, J201.5, J201.10, J201.13, J201.16, R203.1, U201.12 (VSSA), U201.18 (VSS), U201.31 (VSS), U201.47 (VSS), U201.63 (VSS), X201.2 (GND); also elsewhere on the board
unnamed: J202.2, R202.1
unnamed: R201.1, X201.3 (OUT)
unnamed: R203.2, TP201.1, U201.60 (BOOT0)

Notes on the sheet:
24MHz Oscillator
For Bootloader recovery, short BOOT0 (TP201) to 3v3
Pixhawk "Safety Switch" Connector (Hirose DF13-3P-1.25DSA) Internal pull-down resistor on BUTTON Open drain on LED (drive LOW for LED ON)

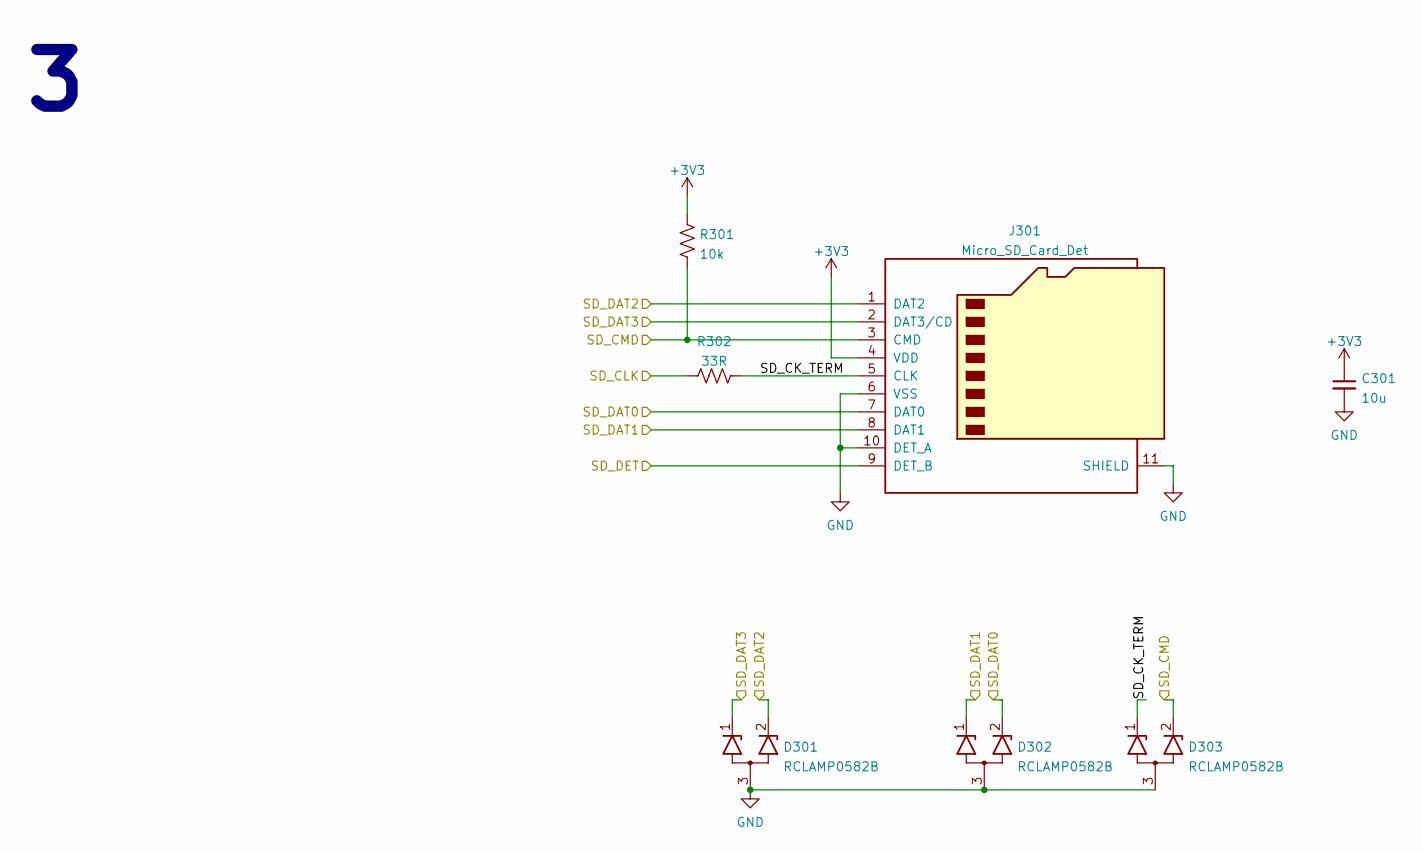
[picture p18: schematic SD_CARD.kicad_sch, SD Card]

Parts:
C301: 10u; C_0805_2012Metric
D301, D302, D303: RCLAMP0582B; SOT-416
J301: Micro_SD_Card_Det; microSD_HC_Molex_104031-0811
R301: 10k; R_0402_1005Metric
R302: 33R; R_0402_1005Metric

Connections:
+3V3: C301.1, J301.4 (VDD), R301.1; also elsewhere on the board
/SD_CARD/SD_CK_TERM: D303.1 (K1), J301.5 (CLK), R302.2
/SD_CARD/SD_CLK: R302.1; also elsewhere on the board
/SD_CARD/SD_CMD: D303.2 (K2), J301.3 (CMD), R301.2; also elsewhere on the board
/SD_CARD/SD_DAT0: D302.2 (K2), J301.7 (DAT0); also elsewhere on the board
/SD_CARD/SD_DAT1: D302.1 (K1), J301.8 (DAT1); also elsewhere on the board
/SD_CARD/SD_DAT2: D301.2 (K2), J301.1 (DAT2); also elsewhere on the board
/SD_CARD/SD_DAT3: D301.1 (K1), J301.2 (DAT3/CD); also elsewhere on the board
/SD_CARD/SD_DET: J301.9 (DET_B); also elsewhere on the board
GND: C301.2, D301.3 (A), D302.3 (A), D303.3 (A), J301.6 (VSS), J301.10 (DET_A), J301.11 (SHIELD); also elsewhere on the board

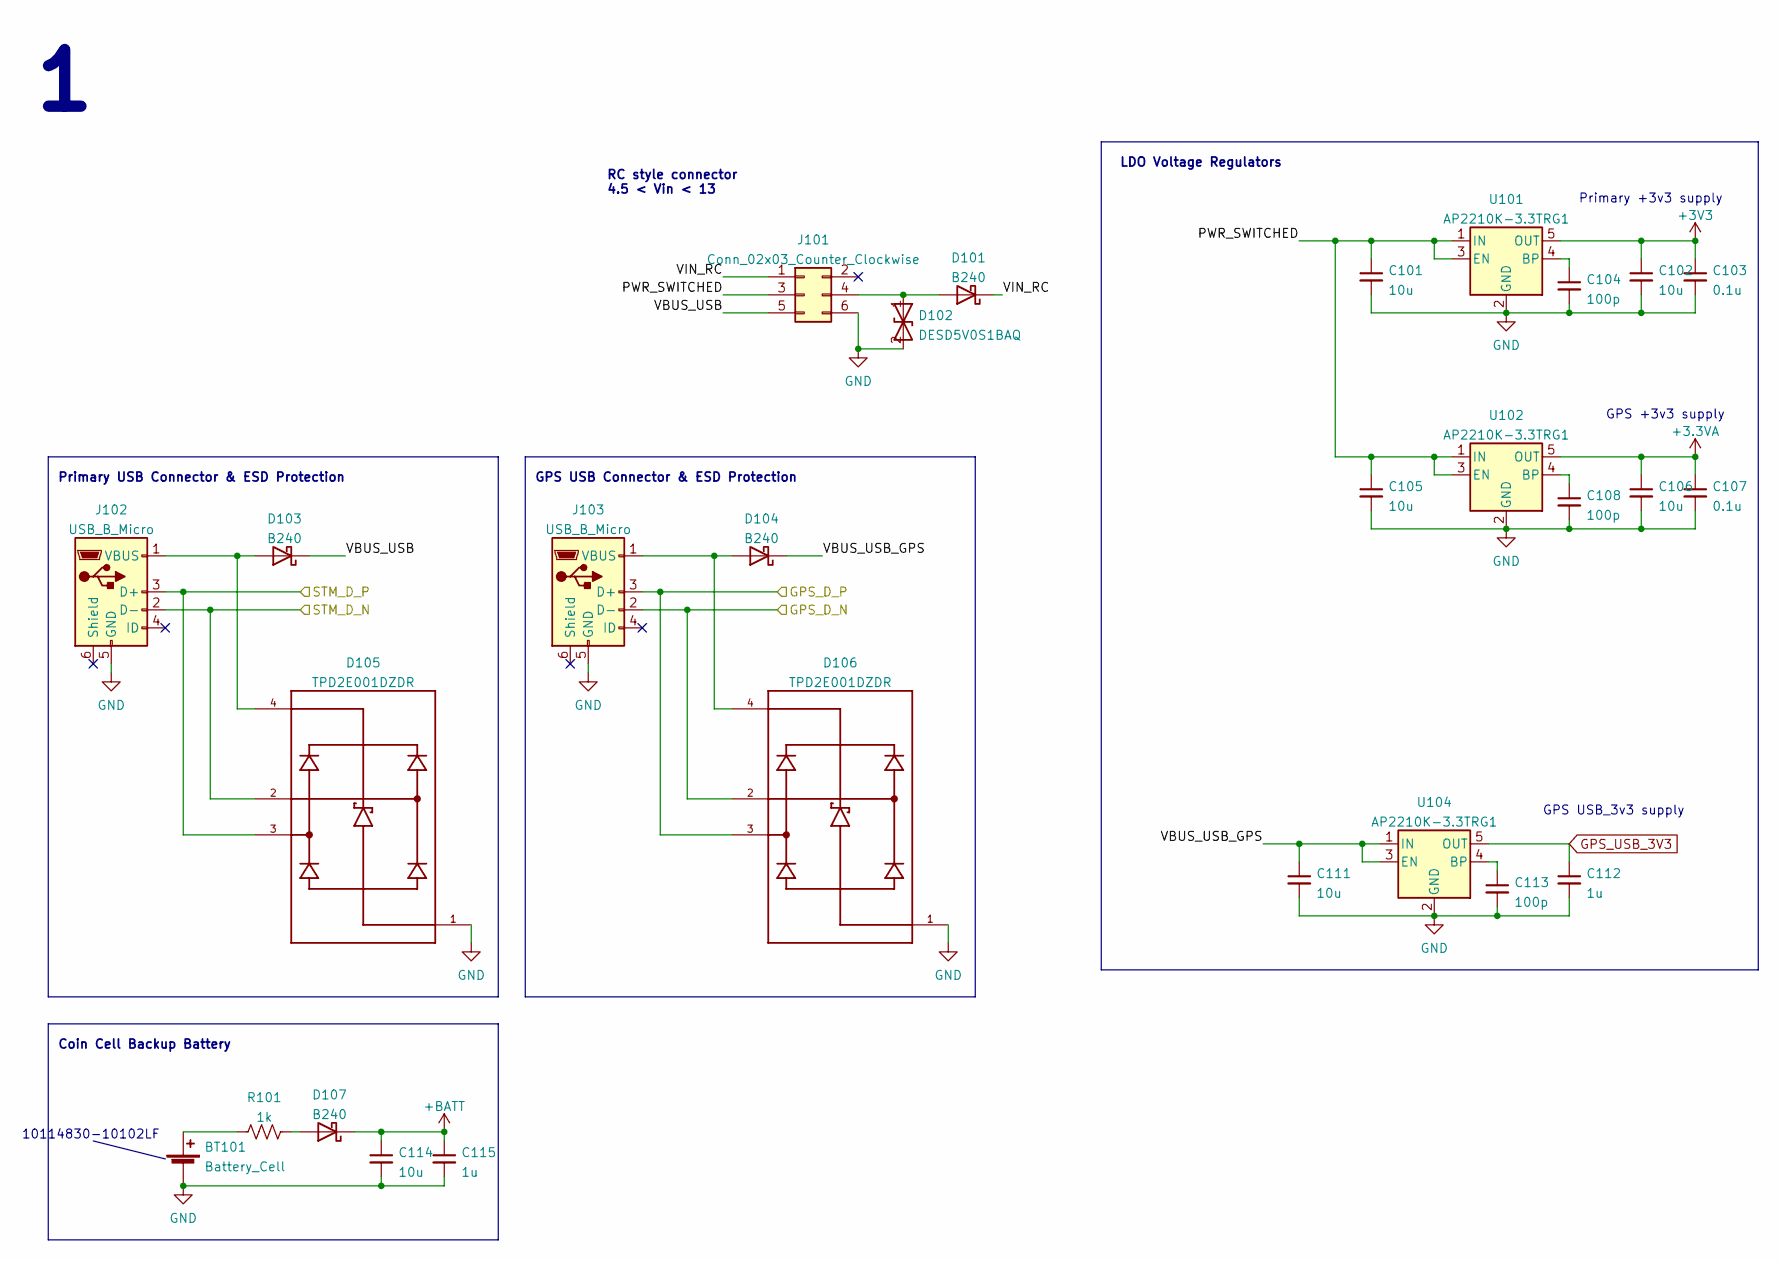
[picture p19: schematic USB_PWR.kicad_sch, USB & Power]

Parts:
BT101: Battery_Cell; Amphenol_10114830-10102LF
C101, C102, C105, C106, C111, C114: 10u; C_0805_2012Metric
C103, C107: 0.1u; C_0402_1005Metric
C104, C108, C113: 100p; C_0402_1005Metric
C112, C115: 1u; C_0402_1005Metric
D101, D103, D104, D107: B240; D_SMB
D102: DESD5V0S1BAQ; D_SOD-323
D105, D106: TPD2E001DZDR; SOT192P237X122-4N; PARTREV I
J101: Conn_02x03_Counter_Clockwise; PinHeader_2x03_P2.54mm_Vertical
J102, J103: USB_B_Micro; USB_Micro-B_Molex_47346-0001
R101: 1k; R_0402_1005Metric
U101, U102, U104: AP2210K-3.3TRG1; SOT-23-5

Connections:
+3.3VA: C106.1, C107.1, U102.5 (OUT); also elsewhere on the board
+3V3: C102.1, C103.1, U101.5 (OUT); also elsewhere on the board
+BATT: C114.1, C115.1, D107.1 (K); also elsewhere on the board
/GPS/GPS_D_N: D106.2, J103.2 (D-); also elsewhere on the board
/GPS/GPS_D_P: D106.3, J103.3 (D+); also elsewhere on the board
/STM32F446/STM_D_N: D105.2, J102.2 (D-); also elsewhere on the board
/STM32F446/STM_D_P: D105.3, J102.3 (D+); also elsewhere on the board
/USB_PWR/PWR_SWITCHED: C101.1, C105.1, J101.3, U101.1 (IN), U101.3 (EN), U102.1 (IN), U102.3 (EN)
/USB_PWR/VBUS_USB: D103.1 (K), J101.5
/USB_PWR/VBUS_USB_GPS: C111.1, D104.1 (K), U104.1 (IN), U104.3 (EN)
/USB_PWR/VIN_RC: D101.1 (K), J101.1
GND: BT101.2 (-), C101.2, C102.2, C103.2, C104.2, C105.2, C106.2, C107.2, C108.2, C111.2, C112.2, C113.2, C114.2, C115.2, D102.2 (A2), D105.1, D106.1, J101.6, J102.5 (GND), J103.5 (GND), U101.2 (GND), U102.2 (GND), U104.2 (GND); also elsewhere on the board
GPS_USB_3V3: C112.1, U104.5 (OUT); also elsewhere on the board
unnamed: BT101.1 (+), R101.1
unnamed: C104.1, U101.4 (BP)
unnamed: C108.1, U102.4 (BP)
unnamed: C113.1, U104.4 (BP)
unnamed: D101.2 (A), D102.1 (A1), J101.4
unnamed: D103.2 (A), D105.4, J102.1 (VBUS)
unnamed: D104.2 (A), D106.4, J103.1 (VBUS)
unnamed: D107.2 (A), R101.2

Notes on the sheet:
GPS USB Connector & ESD Protection
RC style connector 4.5 < Vin < 13
GPS +3v3 supply
Coin Cell Backup Battery
GPS USB_3v3 supply
Primary USB Connector & ESD Protection
LDO Voltage Regulators
Primary +3v3 supply
10114830-10102LF

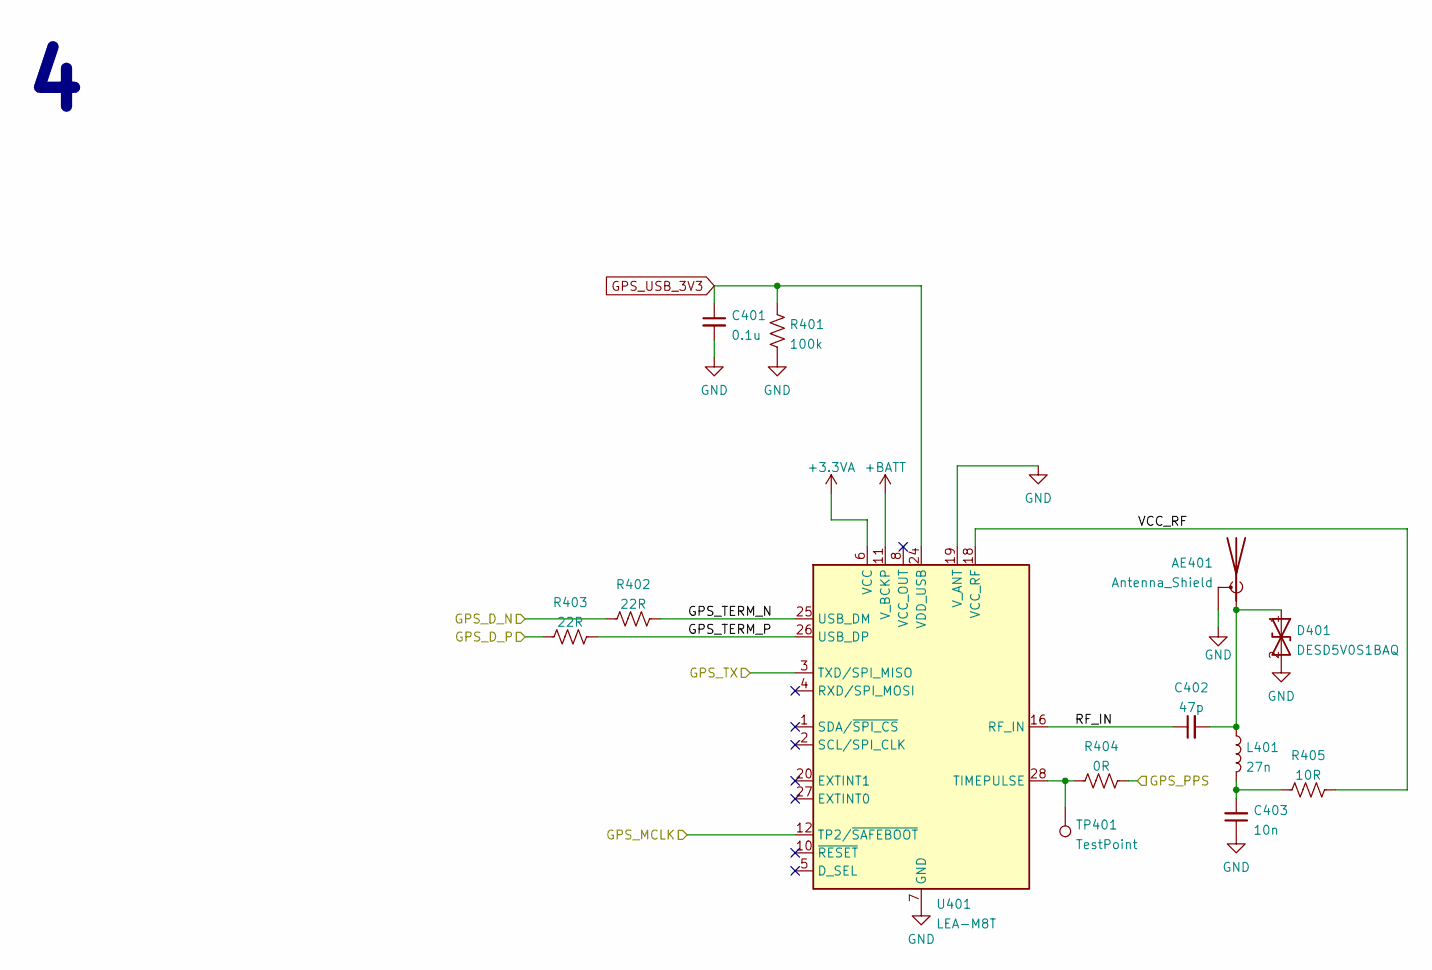
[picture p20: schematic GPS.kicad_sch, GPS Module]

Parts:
AE401: Antenna_Shield; U.FL_Hirose_U.FL-R-SMT-1_Vertical
C401: 0.1u; C_0402_1005Metric
C402: 47p; C_0402_1005Metric
C403: 10n; C_0402_1005Metric
D401: DESD5V0S1BAQ; D_SOD-323
L401: 27n; L_0402_1005Metric
R401: 100k; R_0402_1005Metric
R402, R403: 22R; R_0402_1005Metric
R404: 0R; R_0402_1005Metric
R405: 10R; R_0402_1005Metric
TP401: TestPoint; TestPoint_Pad_D1.5mm
U401: LEA-M8T; ublox_LEA

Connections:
+3.3VA: U401.6 (VCC); also elsewhere on the board
+BATT: U401.11 (V_BCKP); also elsewhere on the board
/BUFFERS/MCLK_IN: U401.12 (TP2/~SAFEBOOT); also elsewhere on the board
/GPS/GPS_D_N: R402.1; also elsewhere on the board
/GPS/GPS_D_P: R403.1; also elsewhere on the board
/GPS/GPS_PPS: R404.2; also elsewhere on the board
/GPS/GPS_TERM_N: R402.2, U401.25 (USB_DM)
/GPS/GPS_TERM_P: R403.2, U401.26 (USB_DP)
/GPS/GPS_TX: U401.3 (TXD/SPI_MISO); also elsewhere on the board
/GPS/RF_IN: C402.1, U401.16 (RF_IN)
/GPS/VCC_RF: R405.2, U401.18 (VCC_RF)
GND: AE401.2 (Shield), C401.2, C403.1, D401.2 (A2), R401.1, U401.7 (GND), U401.13 (GND), U401.14 (GND), U401.15 (GND), U401.17 (GND), U401.19 (V_ANT); also elsewhere on the board
GPS_USB_3V3: C401.1, R401.2, U401.24 (VDD_USB); also elsewhere on the board
unnamed: AE401.1 (A), C402.2, D401.1 (A1), L401.1
unnamed: C403.2, L401.2, R405.1
unnamed: R404.1, TP401.1, U401.28 (TIMEPULSE)

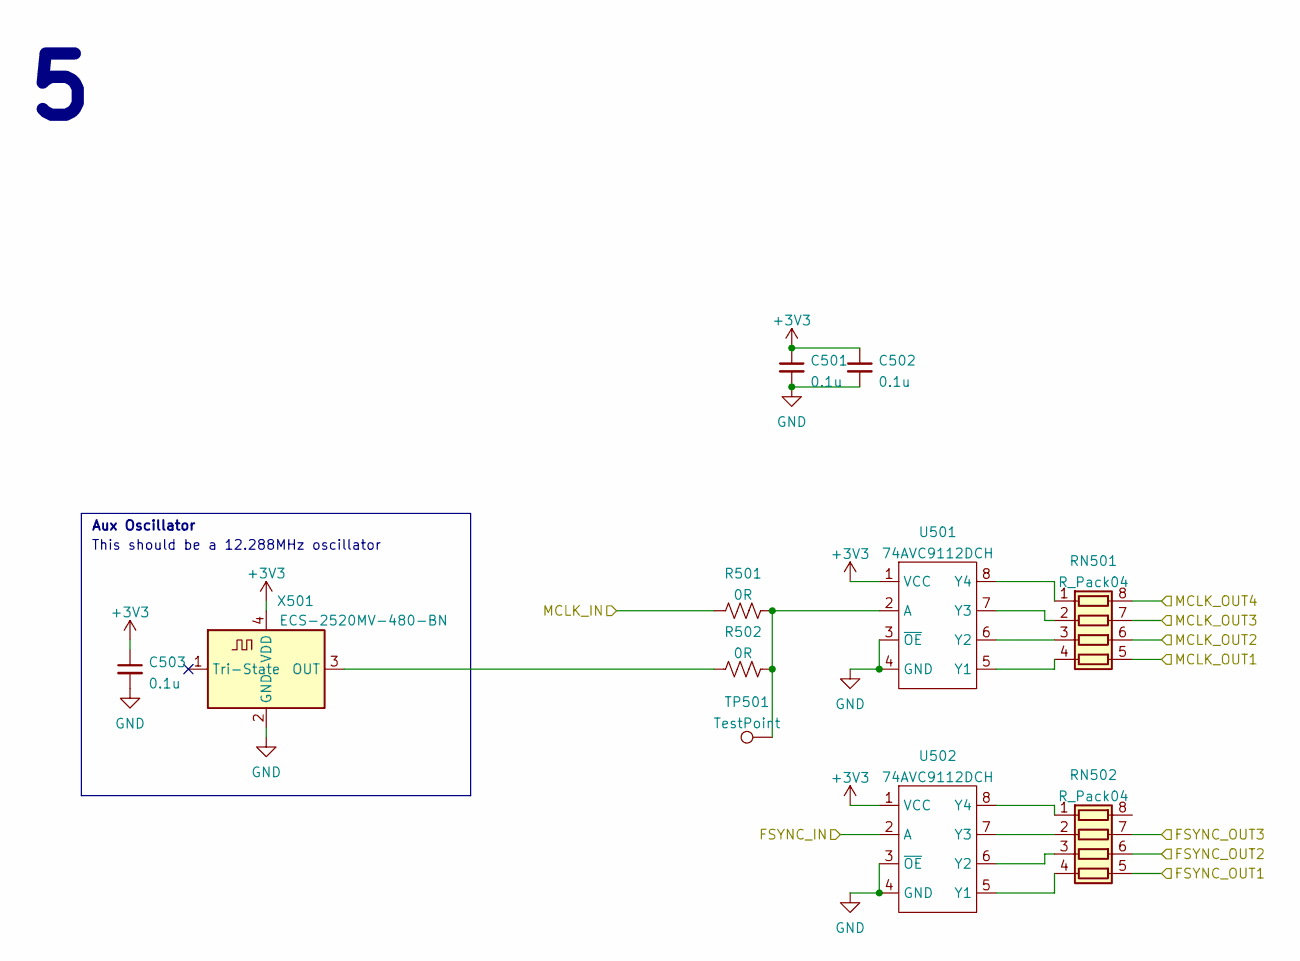
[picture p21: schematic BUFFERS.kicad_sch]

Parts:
C501, C502, C503: 0.1u; C_0402_1005Metric
R501, R502: 0R; R_0402_1005Metric
RN501, RN502: R_Pack04; R_Array_Concave_4x0402
TP501: TestPoint; TestPoint_Pad_D1.5mm
U501, U502: 74AVC9112DCH; VSSOP-8_2.3x2mm_P0.5mm
X501: ECS-2520MV-480-BN; Oscillator_SMD_ECS_2520MV-xxx-xx-4Pin_2.5x2.0mm

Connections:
+3V3: C501.1, C502.1, C503.1, U501.1 (VCC), U502.1 (VCC), X501.4 (VDD); also elsewhere on the board
/BUFFERS/FSYNC_IN: U502.2 (A); also elsewhere on the board
/BUFFERS/FSYNC_OUT1: RN502.5 (R4.2); also elsewhere on the board
/BUFFERS/FSYNC_OUT2: RN502.6 (R3.2); also elsewhere on the board
/BUFFERS/FSYNC_OUT3: RN502.7 (R2.2); also elsewhere on the board
/BUFFERS/MCLK_IN: R501.1; also elsewhere on the board
/BUFFERS/MCLK_OUT1: RN501.5 (R4.2); also elsewhere on the board
/BUFFERS/MCLK_OUT2: RN501.6 (R3.2); also elsewhere on the board
/BUFFERS/MCLK_OUT3: RN501.7 (R2.2); also elsewhere on the board
/BUFFERS/MCLK_OUT4: RN501.8 (R1.2); also elsewhere on the board
GND: C501.2, C502.2, C503.2, U501.3 (~OE), U501.4 (GND), U502.3 (~OE), U502.4 (GND), X501.2 (GND); also elsewhere on the board
unnamed: R501.2, R502.2, TP501.1, U501.2 (A)
unnamed: R502.1, X501.3 (OUT)
unnamed: RN501.1 (R1.1), U501.8 (Y4)
unnamed: RN501.2 (R2.1), U501.7 (Y3)
unnamed: RN501.3 (R3.1), U501.6 (Y2)
unnamed: RN501.4 (R4.1), U501.5 (Y1)
unnamed: RN502.1 (R1.1), U502.8 (Y4)
unnamed: RN502.2 (R2.1), U502.7 (Y3)
unnamed: RN502.3 (R3.1), U502.6 (Y2)
unnamed: RN502.4 (R4.1), U502.5 (Y1)

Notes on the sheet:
This should be a 12.288MHz oscillator
Aux Oscillator

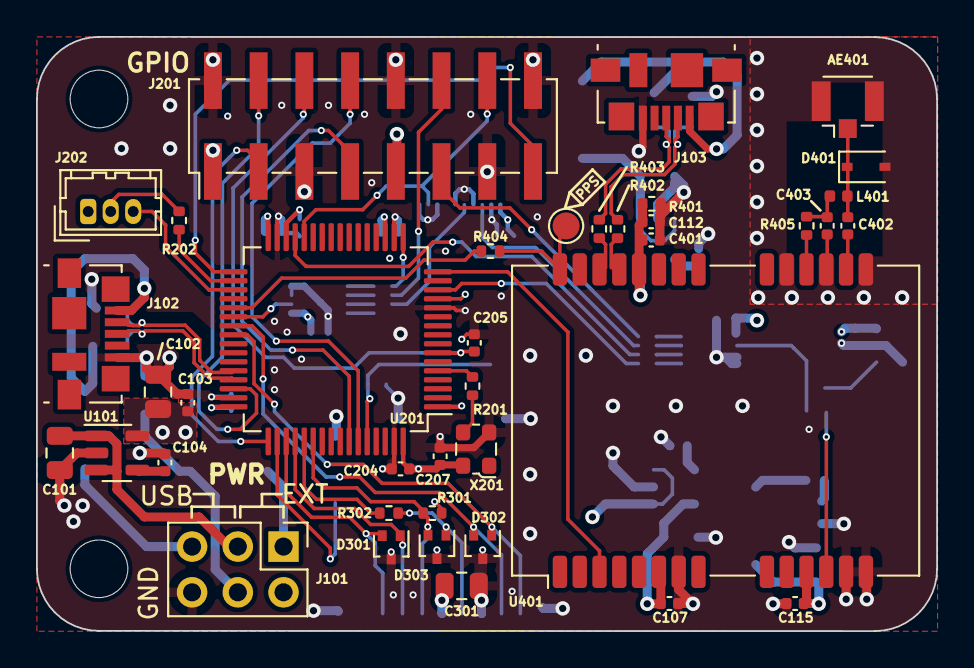
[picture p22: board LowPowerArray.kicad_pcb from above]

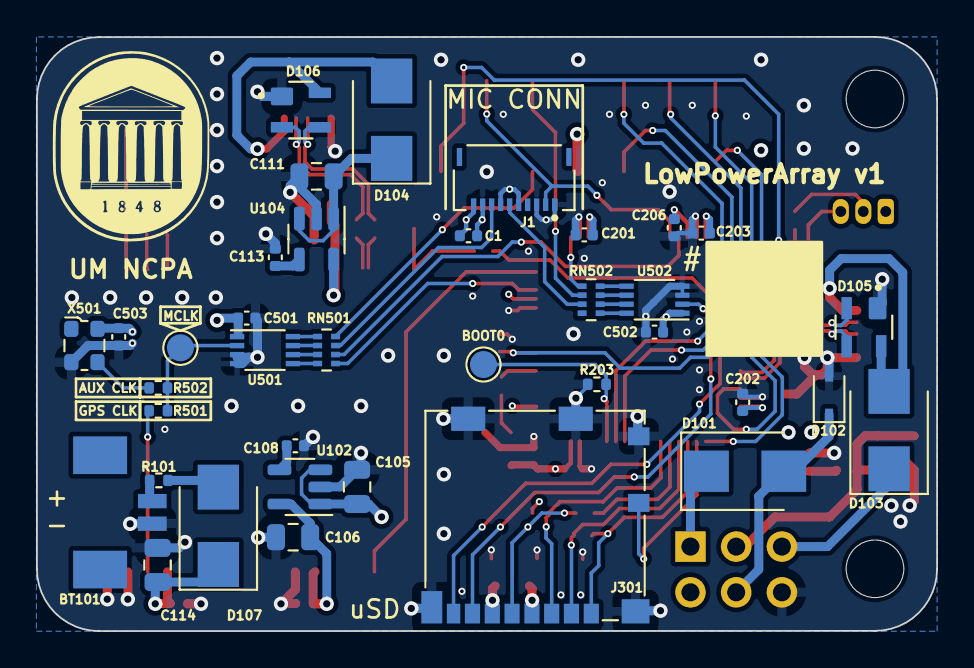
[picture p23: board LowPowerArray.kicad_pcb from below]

Board: 6 copper layers, 50.0 x 33.0 mm, 78 parts (37 on the bottom side), 71 nets.

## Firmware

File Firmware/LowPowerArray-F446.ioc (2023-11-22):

#MicroXplorer Configuration settings - do not modify
Dma.Request0=SDIO
Dma.Request1=SAI1_A
Dma.Request2=USART2_RX
Dma.RequestsNb=3
Dma.SAI1_A.1.Direction=DMA_PERIPH_TO_MEMORY
Dma.SAI1_A.1.FIFOMode=DMA_FIFOMODE_ENABLE
Dma.SAI1_A.1.FIFOThreshold=DMA_FIFO_THRESHOLD_FULL
Dma.SAI1_A.1.Instance=DMA2_Stream1
Dma.SAI1_A.1.MemBurst=DMA_MBURST_SINGLE
Dma.SAI1_A.1.MemDataAlignment=DMA_MDATAALIGN_WORD
Dma.SAI1_A.1.MemInc=DMA_MINC_ENABLE
Dma.SAI1_A.1.Mode=DMA_NORMAL
Dma.SAI1_A.1.PeriphBurst=DMA_PBURST_SINGLE
Dma.SAI1_A.1.PeriphDataAlignment=DMA_PDATAALIGN_WORD
Dma.SAI1_A.1.PeriphInc=DMA_PINC_DISABLE
Dma.SAI1_A.1.Priority=DMA_PRIORITY_VERY_HIGH
Dma.SAI1_A.1.RequestParameters=Instance,Direction,PeriphInc,MemInc,PeriphDataAlignment,MemDataAlignment,Mode,Priority,FIFOMode,FIFOThreshold,MemBurst,PeriphBurst
Dma.SDIO.0.Direction=DMA_PERIPH_TO_MEMORY
Dma.SDIO.0.FIFOMode=DMA_FIFOMODE_ENABLE
Dma.SDIO.0.FIFOThreshold=DMA_FIFO_THRESHOLD_FULL
Dma.SDIO.0.Instance=DMA2_Stream3
Dma.SDIO.0.MemBurst=DMA_MBURST_SINGLE
Dma.SDIO.0.MemDataAlignment=DMA_MDATAALIGN_WORD
Dma.SDIO.0.MemInc=DMA_MINC_ENABLE
Dma.SDIO.0.Mode=DMA_PFCTRL
Dma.SDIO.0.PeriphBurst=DMA_PBURST_INC4
Dma.SDIO.0.PeriphDataAlignment=DMA_PDATAALIGN_WORD
Dma.SDIO.0.PeriphInc=DMA_PINC_DISABLE
Dma.SDIO.0.Priority=DMA_PRIORITY_VERY_HIGH
Dma.SDIO.0.RequestParameters=Instance,Direction,PeriphInc,MemInc,PeriphDataAlignment,MemDataAlignment,Mode,Priority,FIFOMode,FIFOThreshold,MemBurst,PeriphBurst
Dma.USART2_RX.2.Direction=DMA_PERIPH_TO_MEMORY
Dma.USART2_RX.2.FIFOMode=DMA_FIFOMODE_DISABLE
Dma.USART2_RX.2.Instance=DMA1_Stream5
Dma.USART2_RX.2.MemDataAlignment=DMA_MDATAALIGN_BYTE
Dma.USART2_RX.2.MemInc=DMA_MINC_ENABLE
Dma.USART2_RX.2.Mode=DMA_NORMAL
Dma.USART2_RX.2.PeriphDataAlignment=DMA_PDATAALIGN_BYTE
Dma.USART2_RX.2.PeriphInc=DMA_PINC_DISABLE
Dma.USART2_RX.2.Priority=DMA_PRIORITY_LOW
Dma.USART2_RX.2.RequestParameters=Instance,Direction,PeriphInc,MemInc,PeriphDataAlignment,MemDataAlignment,Mode,Priority,FIFOMode
FATFS.BSP.number=1
FATFS.IPParameters=_USE_LFN,_MAX_SS,_FS_EXFAT,USE_DMA_CODE_SD,_USE_EXPAND,_USE_FIND
FATFS.USE_DMA_CODE_SD=1
FATFS._FS_EXFAT=1
FATFS._MAX_SS=4096
FATFS._USE_EXPAND=1
FATFS._USE_FIND=1
FATFS._USE_LFN=2
FATFS0.BSP.STBoard=false
FATFS0.BSP.api=Unknown
FATFS0.BSP.component=
FATFS0.BSP.condition=
FATFS0.BSP.instance=PA15
FATFS0.BSP.ip=GPIO
FATFS0.BSP.mode=Input
FATFS0.BSP.name=Detect_SDIO
FATFS0.BSP.semaphore=
FATFS0.BSP.solution=PA15
File.Version=6
GPIO.groupedBy=Group By Peripherals
KeepUserPlacement=false
Mcu.CPN=STM32F446RET6
Mcu.Family=STM32F4
Mcu.IP0=DMA
Mcu.IP1=FATFS
Mcu.IP10=USB_DEVICE
Mcu.IP11=USB_OTG_FS
Mcu.IP2=NVIC
Mcu.IP3=RCC
Mcu.IP4=SAI1
Mcu.IP5=SDIO
Mcu.IP6=SYS
Mcu.IP7=TIM8
Mcu.IP8=USART1
Mcu.IP9=USART2
Mcu.IPNb=12
Mcu.Name=STM32F446R(C-E)Tx
Mcu.Package=LQFP64
Mcu.Pin0=PH0-OSC_IN
Mcu.Pin1=PH1-OSC_OUT
Mcu.Pin10=PC6
Mcu.Pin11=PC7
Mcu.Pin12=PC8
Mcu.Pin13=PC9
Mcu.Pin14=PA11
Mcu.Pin15=PA12
Mcu.Pin16=PA13
Mcu.Pin17=PA14
Mcu.Pin18=PA15
Mcu.Pin19=PC10
Mcu.Pin2=PA0-WKUP
Mcu.Pin20=PC11
Mcu.Pin21=PC12
Mcu.Pin22=PD2
Mcu.Pin23=PB6
Mcu.Pin24=PB7
Mcu.Pin25=VP_FATFS_VS_SDIO
Mcu.Pin26=VP_TIM8_VS_ControllerModeTrigger
Mcu.Pin27=VP_USB_DEVICE_VS_USB_DEVICE_CDC_FS
Mcu.Pin3=PA2
Mcu.Pin4=PA3
Mcu.Pin5=PB2
Mcu.Pin6=PB10
Mcu.Pin7=PB12
Mcu.Pin8=PB13
Mcu.Pin9=PB14
Mcu.PinsNb=28
Mcu.ThirdPartyNb=0
Mcu.UserConstants=
Mcu.UserName=STM32F446RETx
MxCube.Version=6.6.1
MxDb.Version=DB.6.0.60
NVIC.BusFault_IRQn=true\:0\:0\:false\:false\:true\:false\:false\:false
NVIC.DMA1_Stream5_IRQn=true\:3\:0\:true\:false\:true\:false\:true\:true
NVIC.DMA2_Stream1_IRQn=true\:0\:0\:true\:false\:true\:false\:true\:true
NVIC.DMA2_Stream3_IRQn=true\:1\:0\:true\:false\:true\:false\:true\:true
NVIC.DebugMonitor_IRQn=true\:0\:0\:false\:false\:true\:false\:false\:false
NVIC.EXTI15_10_IRQn=true\:7\:0\:true\:false\:true\:true\:true\:true
NVIC.ForceEnableDMAVector=true
NVIC.HardFault_IRQn=true\:0\:0\:false\:false\:true\:false\:false\:false
NVIC.MemoryManagement_IRQn=true\:0\:0\:false\:false\:true\:false\:false\:false
NVIC.NonMaskableInt_IRQn=true\:0\:0\:false\:false\:true\:false\:false\:false
NVIC.OTG_FS_IRQn=true\:2\:0\:true\:false\:true\:false\:true\:true
NVIC.PendSV_IRQn=true\:0\:0\:false\:false\:true\:false\:false\:false
NVIC.PriorityGroup=NVIC_PRIORITYGROUP_4
NVIC.SAI1_IRQn=true\:0\:0\:false\:false\:true\:true\:true\:true
NVIC.SDIO_IRQn=true\:1\:0\:true\:false\:true\:true\:true\:true
NVIC.SVCall_IRQn=true\:0\:0\:false\:false\:true\:false\:false\:false
NVIC.SysTick_IRQn=true\:15\:0\:false\:false\:true\:false\:true\:false
NVIC.USART2_IRQn=true\:4\:0\:true\:false\:true\:true\:true\:true
NVIC.UsageFault_IRQn=true\:0\:0\:false\:false\:true\:false\:false\:false
PA0-WKUP.Signal=S_TIM8_ETR
PA11.Mode=Device_Only
PA11.Signal=USB_OTG_FS_DM
PA12.Mode=Device_Only
PA12.Signal=USB_OTG_FS_DP
PA13.Mode=Serial_Wire
PA13.Signal=SYS_JTMS-SWDIO
PA14.Mode=Serial_Wire
PA14.Signal=SYS_JTCK-SWCLK
PA15.GPIOParameters=GPIO_PuPd,GPIO_Label
PA15.GPIO_Label=SD_DETECT
PA15.GPIO_PuPd=GPIO_PULLUP
PA15.Locked=true
PA15.Signal=GPIO_Input
PA2.Locked=true
PA2.Mode=Half_duplex(single_wire_mode)
PA2.Signal=USART2_TX
PA3.Mode=SAI_A_AsyncSlave
PA3.Signal=SAI1_FS_A
PB10.Mode=SAI_A_AsyncSlave
PB10.Signal=SAI1_SCK_A
PB12.GPIOParameters=GPIO_PuPd,GPIO_Label
PB12.GPIO_Label=MODE_SEL
PB12.GPIO_PuPd=GPIO_PULLUP
PB12.Locked=true
PB12.Signal=GPIO_Input
PB13.GPIOParameters=PinState,GPIO_PuPd,GPIO_Label,GPIO_ModeDefaultOutputPP
PB13.GPIO_Label=USER_LED
PB13.GPIO_ModeDefaultOutputPP=GPIO_MODE_OUTPUT_OD
PB13.GPIO_PuPd=GPIO_NOPULL
PB13.Locked=true
PB13.PinState=GPIO_PIN_RESET
PB13.Signal=GPIO_Output
PB14.GPIOParameters=GPIO_PuPd,GPIO_Label
PB14.GPIO_Label=USER_BTN
PB14.GPIO_PuPd=GPIO_PULLDOWN
PB14.Locked=true
PB14.Signal=GPXTI14
PB2.GPIOParameters=GPIO_PuPd
PB2.GPIO_PuPd=GPIO_NOPULL
PB2.Locked=true
PB2.Mode=SAI_A_AsyncSlave
PB2.Signal=SAI1_SD_A
PB6.Locked=true
PB6.Mode=Asynchronous
PB6.Signal=USART1_TX
PB7.Locked=true
PB7.Mode=Asynchronous
PB7.Signal=USART1_RX
PC10.GPIOParameters=GPIO_PuPd
PC10.GPIO_PuPd=GPIO_PULLUP
PC10.Locked=true
PC10.Mode=SD_4_bits_Wide_bus
PC10.Signal=SDIO_D2
PC11.GPIOParameters=GPIO_PuPd
PC11.GPIO_PuPd=GPIO_PULLUP
PC11.Mode=SD_4_bits_Wide_bus
PC11.Signal=SDIO_D3
PC12.Locked=true
PC12.Mode=SD_4_bits_Wide_bus
PC12.Signal=SDIO_CK
PC6.GPIOParameters=GPIO_Label,GPIO_ModeDefaultEXTI
PC6.GPIO_Label=PPS_INPUT
PC6.GPIO_ModeDefaultEXTI=GPIO_MODE_IT_FALLING
PC6.Locked=true
PC6.Signal=S_TIM8_CH1
PC7.GPIOParameters=GPIO_Speed,GPIO_Label
PC7.GPIO_Label=TIM_FSYNC_OUT
PC7.GPIO_Speed=GPIO_SPEED_FREQ_VERY_HIGH
PC7.Locked=true
PC7.Signal=S_TIM8_CH2
PC8.GPIOParameters=GPIO_PuPd
PC8.GPIO_PuPd=GPIO_PULLUP
PC8.Mode=SD_4_bits_Wide_bus
PC8.Signal=SDIO_D0
PC9.GPIOParameters=GPIO_PuPd
PC9.GPIO_PuPd=GPIO_PULLUP
PC9.Locked=true
PC9.Mode=SD_4_bits_Wide_bus
PC9.Signal=SDIO_D1
PD2.Mode=SD_4_bits_Wide_bus
PD2.Signal=SDIO_CMD
PH0-OSC_IN.Mode=HSE-External-Clock-Source
PH0-OSC_IN.Signal=RCC_OSC_IN
PH1-OSC_OUT.Mode=HSE-External-Clock-Source
PH1-OSC_OUT.Signal=RCC_OSC_OUT
PinOutPanel.RotationAngle=0
ProjectManager.AskForMigrate=true
ProjectManager.BackupPrevious=false
ProjectManager.CompilerOptimize=6
ProjectManager.ComputerToolchain=false
ProjectManager.CoupleFile=false
ProjectManager.CustomerFirmwarePackage=
ProjectManager.DefaultFWLocation=true
ProjectManager.DeletePrevious=true
ProjectManager.DeviceId=STM32F446RETx
ProjectManager.FirmwarePackage=STM32Cube FW_F4 V1.27.1
ProjectManager.FreePins=false
ProjectManager.HalAssertFull=false
ProjectManager.HeapSize=0x200
ProjectManager.KeepUserCode=true
ProjectManager.LastFirmware=true
ProjectManager.LibraryCopy=1
ProjectManager.MainLocation=Core/Src
ProjectManager.NoMain=false
ProjectManager.PreviousToolchain=
ProjectManager.ProjectBuild=false
ProjectManager.ProjectFileName=LowPowerArray-F446.ioc
ProjectManager.ProjectName=LowPowerArray-F446
ProjectManager.RegisterCallBack=
ProjectManager.StackSize=0x400
ProjectManager.TargetToolchain=STM32CubeIDE
ProjectManager.ToolChainLocation=
ProjectManager.UnderRoot=true
ProjectManager.functionlistsort=1-SystemClock_Config-RCC-false-HAL-false,2-MX_GPIO_Init-GPIO-false-HAL-true,3-MX_DMA_Init-DMA-false-HAL-true,4-MX_USART1_UART_Init-USART1-false-HAL-true,5-MX_USART2_UART_Init-USART2-false-HAL-true,6-MX_TIM8_Init-TIM8-false-HAL-true,7-MX_SDIO_SD_Init-SDIO-false-HAL-true,8-MX_FATFS_Init-FATFS-false-HAL-false,9-MX_SAI1_Init-SAI1-false-HAL-true,10-MX_USB_DEVICE_Init-USB_DEVICE-false-HAL-false
RCC.AHBFreq_Value=168000000
RCC.APB1CLKDivider=RCC_HCLK_DIV4
RCC.APB1Freq_Value=42000000
RCC.APB1TimFreq_Value=84000000
RCC.APB2CLKDivider=RCC_HCLK_DIV2
RCC.APB2Freq_Value=84000000
RCC.APB2TimFreq_Value=168000000
RCC.CECFreq_Value=32786.88524590164
RCC.CortexFreq_Value=168000000
RCC.DATA_CACHE_ENABLE=1
RCC.FCLKCortexFreq_Value=168000000
RCC.FMPI2C1Freq_Value=42000000
RCC.FamilyName=M
RCC.HCLKFreq_Value=168000000
RCC.HSE_VALUE=24000000
RCC.I2S1Freq_Value=50000000
RCC.I2S2Freq_Value=50000000
RCC.IPParameters=AHBFreq_Value,APB1CLKDivider,APB1Freq_Value,APB1TimFreq_Value,APB2CLKDivider,APB2Freq_Value,APB2TimFreq_Value,CECFreq_Value,CortexFreq_Value,DATA_CACHE_ENABLE,FCLKCortexFreq_Value,FMPI2C1Freq_Value,FamilyName,HCLKFreq_Value,HSE_VALUE,I2S1Freq_Value,I2S2Freq_Value,MCO2PinFreq_Value,PLLCLKFreq_Value,PLLI2SM,PLLI2SN,PLLI2SPCLKFreq_Value,PLLI2SQCLKFreq_Value,PLLI2SRCLKFreq_Value,PLLI2SoutputFreq_Value,PLLM,PLLN,PLLQ,PLLQCLKFreq_Value,PLLRCLKFreq_Value,PLLSAIM,PLLSAIN,PLLSAIPCLKFreq_Value,PLLSAIQCLKFreq_Value,PLLSAIoutputFreq_Value,PLLSourceVirtual,PWRFreq_Value,SAIACLockSelection,SAIAFreq_Value,SAIBFreq_Value,SDIOFreq_Value,SPDIFRXFreq_Value,SYSCLKFreq_VALUE,SYSCLKSource,USBFreq_Value,VCOI2SInputFreq_Value,VCOI2SOutputFreq_Value,VCOInputFreq_Value,VCOOutputFreq_Value,VCOSAIInputFreq_Value,VCOSAIOutputFreq_Value
RCC.MCO2PinFreq_Value=168000000
RCC.PLLCLKFreq_Value=168000000
RCC.PLLI2SM=12
RCC.PLLI2SN=50
RCC.PLLI2SPCLKFreq_Value=50000000
RCC.PLLI2SQCLKFreq_Value=50000000
RCC.PLLI2SRCLKFreq_Value=50000000
RCC.PLLI2SoutputFreq_Value=50000000
RCC.PLLM=12
RCC.PLLN=168
RCC.PLLQ=7
RCC.PLLQCLKFreq_Value=48000000
RCC.PLLRCLKFreq_Value=168000000
RCC.PLLSAIM=12
RCC.PLLSAIN=50
RCC.PLLSAIPCLKFreq_Value=50000000
RCC.PLLSAIQCLKFreq_Value=50000000
RCC.PLLSAIoutputFreq_Value=50000000
RCC.PLLSourceVirtual=RCC_PLLSOURCE_HSE
RCC.PWRFreq_Value=168000000
RCC.SAIACLockSelection=RCC_SAI1CLKSOURCE_PLLR
RCC.SAIAFreq_Value=168000000
RCC.SAIBFreq_Value=50000000
RCC.SDIOFreq_Value=48000000
RCC.SPDIFRXFreq_Value=168000000
RCC.SYSCLKFreq_VALUE=168000000
RCC.SYSCLKSource=RCC_SYSCLKSOURCE_PLLCLK
RCC.USBFreq_Value=48000000
RCC.VCOI2SInputFreq_Value=2000000
RCC.VCOI2SOutputFreq_Value=100000000
RCC.VCOInputFreq_Value=2000000
RCC.VCOOutputFreq_Value=336000000
RCC.VCOSAIInputFreq_Value=2000000
RCC.VCOSAIOutputFreq_Value=100000000
SAI1.ActiveFrameLength-SAI_A_AsyncSlave=31
SAI1.ClockStrobing-SAI_A_AsyncSlave=SAI_CLOCKSTROBING_FALLINGEDGE
SAI1.CompandingMode-SAI_A_AsyncSlave=SAI_NOCOMPANDING
SAI1.DataSize-SAI_A_AsyncSlave=SAI_DATASIZE_32
SAI1.FIFOThreshold-SAI_A_AsyncSlave=SAI_FIFOTHRESHOLD_FULL
SAI1.FSDefinition-SAI_A_AsyncSlave=SAI_FS_STARTFRAME
SAI1.FSOffset-SAI_A_AsyncSlave=SAI_FS_FIRSTBIT
SAI1.FSPolarity-SAI_A_AsyncSlave=SAI_FS_ACTIVE_HIGH
SAI1.FirstBitOffset-SAI_A_AsyncSlave=0
SAI1.FrameLength-SAI_A_AsyncSlave=256
SAI1.IPParameters=Instance-SAI_A_AsyncSlave,VirtualMode-SAI_A_AsyncSlave,FrameLength-SAI_A_AsyncSlave,DataSize-SAI_A_AsyncSlave,SlotSize-SAI_A_AsyncSlave,FSPolarity-SAI_A_AsyncSlave,SlotNumber-SAI_A_AsyncSlave,VirtualSlotActive-SAI_A_AsyncSlave,FIFOThreshold-SAI_A_AsyncSlave,ActiveFrameLength-SAI_A_AsyncSlave,TriState-SAI_A_AsyncSlave,FSOffset-SAI_A_AsyncSlave,FirstBitOffset-SAI_A_AsyncSlave,CompandingMode-SAI_A_AsyncSlave,ClockStrobing-SAI_A_AsyncSlave,FSDefinition-SAI_A_AsyncSlave,SlotActive-SAI_A_AsyncSlave
SAI1.Instance-SAI_A_AsyncSlave=SAI$Index_Block_A
SAI1.SlotActive-SAI_A_AsyncSlave=0x0000FFFF
SAI1.SlotNumber-SAI_A_AsyncSlave=8
SAI1.SlotSize-SAI_A_AsyncSlave=SAI_SLOTSIZE_32B
SAI1.TriState-SAI_A_AsyncSlave=SAI_OUTPUT_NOTRELEASED
SAI1.VirtualMode-SAI_A_AsyncSlave=VM_SLAVE
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

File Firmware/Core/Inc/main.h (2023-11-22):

/* USER CODE BEGIN Header */
/**
  ******************************************************************************
  * @file           : main.h
  * @brief          : Header for main.c file.
  *                   This file contains the common defines of the application.
  ******************************************************************************
  * @attention
  *
  * Copyright (c) 2023 STMicroelectronics.
  * All rights reserved.
  *
  * This software is licensed under terms that can be found in the LICENSE file
  * in the root directory of this software component.
  * If no LICENSE file comes with this software, it is provided AS-IS.
  *
  ******************************************************************************
  */
/* USER CODE END Header */

/* Define to prevent recursive inclusion -------------------------------------*/
#ifndef __MAIN_H
#define __MAIN_H

#ifdef __cplusplus
extern "C" {
#endif

/* Includes ------------------------------------------------------------------*/
#include "stm32f4xx_hal.h"

/* Private includes ----------------------------------------------------------*/
/* USER CODE BEGIN Includes */

/* USER CODE END Includes */

/* Exported types ------------------------------------------------------------*/
/* USER CODE BEGIN ET */

/* USER CODE END ET */

/* Exported constants --------------------------------------------------------*/
/* USER CODE BEGIN EC */

/* USER CODE END EC */

/* Exported macro ------------------------------------------------------------*/
/* USER CODE BEGIN EM */

/* USER CODE END EM */

void HAL_TIM_MspPostInit(TIM_HandleTypeDef *htim);

/* Exported functions prototypes ---------------------------------------------*/
void Error_Handler(void);

/* USER CODE BEGIN EFP */

/* USER CODE END EFP */

/* Private defines -----------------------------------------------------------*/
#define MODE_SEL_Pin GPIO_PIN_12
#define MODE_SEL_GPIO_Port GPIOB
#define USER_LED_Pin GPIO_PIN_13
#define USER_LED_GPIO_Port GPIOB
#define USER_BTN_Pin GPIO_PIN_14
#define USER_BTN_GPIO_Port GPIOB
#define USER_BTN_EXTI_IRQn EXTI15_10_IRQn
#define PPS_INPUT_Pin GPIO_PIN_6
#define PPS_INPUT_GPIO_Port GPIOC
#define TIM_FSYNC_OUT_Pin GPIO_PIN_7
#define TIM_FSYNC_OUT_GPIO_Port GPIOC
#define SD_DETECT_Pin GPIO_PIN_15
#define SD_DETECT_GPIO_Port GPIOA
/* USER CODE BEGIN Private defines */

/* USER CODE END Private defines */

#ifdef __cplusplus
}
#endif

#endif /* __MAIN_H */
